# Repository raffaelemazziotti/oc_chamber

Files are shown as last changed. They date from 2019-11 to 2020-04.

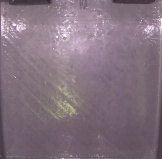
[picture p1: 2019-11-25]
LCD_oc_chamber/template.jpg

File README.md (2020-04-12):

# Operant Conditioning Chamber

Operant conditioning is a classical paradigm used in experimental psychology in which animals learn to perform an action in order to achieve a reward. By using this paradigm, it is possible to extract learning curves and measure accurately reaction times.
Here we describe a fully 3D printable device that is able to perform operant conditioning on  freely moving mice, while performing real-time tracking of the animal position.

## Assembling & Installation

You can find 3D printed models [here](https://github.com/raffaelemazziotti/oc_chamber/tree/master/3D_models) or [here](https://www.thingiverse.com/thing:3975752).  
In [figures/EXPLODED VIEW.jpg](https://github.com/raffaelemazziotti/oc_chamber/blob/master/figures/EXPLODED%20VIEW.jpg) there is an intuitive diagram of the assembling scheme.
We printed all the components using Cura 4.0 with a medium resolution (100 µm), a speed of 90 mm/s and an infill of 20%. The design of the OC chamber is quite simple so almost all the printers are sufficiently precise to successfully print the entire chamber.

A list of all the components can be found here: [Bill of materials](https://docs.google.com/spreadsheets/d/19AH2Pe1oMEcGUEE4mrs1yGA2-vNfwtRM7asQJUQdpgM/edit?usp=sharing)

### 3D printed parts

* **OC CHAMBER**
  * **arena:** main arena
  * **arena_holes:** main arena with holes on the floor
  * **barrier_posterior:** posterior barrier for jumpig mice
  * **frontal_wall_LED:** interface wall for LED matrix
  * **frontal_wall_LCD:** interface wall for LCD screen
  * **mask_dots:** mask for LED matrix
  * **touch_sensor:** button
* **CAMERA**
  * **cam_barrier:** camera holder with frontal barrrier for jumping mice
  * **cam_ladder:** 3d printed arm
  * **cam_holder:** camera holder
  
* **DELIVERY**
  * **delivery_base:** syringe and motor holders
  * **delivery_motor2thread:** thread to motor adapter
  * **delivery_piston:** syringe piston

In addition you need:

* a 1000 µF capacitor
* two 25 Mohm resistors for the touch buttons
* a 220 ohm resistor for the LED matrix
* a piece of M8 thread (~15 cm) for reward delivery

Connect all the components as described in [figures/diagram_scheme.png](https://github.com/raffapaz/oc_chamber/blob/master/figures/diagram_scheme.png)

To install the software in the Raspberry Pi(RPI) just download or copy the entire code in a folder of the Raspian OS.  

### Required libraries

Python

* [picamera](https://picamera.readthedocs.io/en/release-1.13/)
* [pySerial](https://pythonhosted.org/pyserial/)
* [openCV](https://pypi.org/project/opencv-python/)
* [Tkinter](https://tkdocs.com/tutorial/install.html)

Arduino

* [CapacitiveSensor](https://playground.arduino.cc/Main/CapacitiveSensor/)
* [Adafruit_NeoPixel](https://learn.adafruit.com/adafruit-neopixel-uberguide/arduino-library-use)
* [Stepper](https://www.arduino.cc/en/reference/stepper)

### Arduino Configuration

Compile and load on the [Arduino UNO](https://store.arduino.cc/arduino-uno-rev3) the sketch called [skinner.ino](https://github.com/raffaelemazziotti/oc_chamber/tree/master/arduino_files/skinner)

### Capacitive Sensors calibration

To calibrate [capacitive sensors](https://en.wikipedia.org/wiki/Capacitive_sensing) thresholds load the Arduino sketch called [skinnerCapacitiveTest](https://github.com/raffaelemazziotti/oc_chamber/tree/master/arduino_files/skinnerCapacitiveTest). This function just prints on the serial port capacitive sensor values. It is helpful to set the proper threshold value to detect mouse touches.

### Running Python code

To run the code type in terminal:

```bash
cd \home\pi\oc_chamber\         \\ or replace with the folder path containing the scpript
python3 cvConditioningTracking.py
```

Alternatively open cvConditioningTracking in [IDLE](https://en.wikipedia.org/wiki/IDLE) IDE and push F5.

The user can customize some of the low-level parameters of the experiments by editing the value of the variables in the first 25 lines of the file [cvConditioningTracking](https://github.com/raffaelemazziotti/oc_chamber/blob/master/cvConditioningTracking.py).py. A more detailed explanation of those parameters is given in the file itself.

The chamber can run experiments in 2 modes: **Training** mode and **Permutation** mode. The user can select one of the two modes by editing the parameter **task** in the cvConditioningTracking file. The details and differences of the 2 modes can be found in the [paper](#references).

### Experiment info GUI

At the start of the experiments, the user is prompted with a GUI that collects some basic informations about the experiments that is about to run.

Screenshot of the GUI for selecting some basic experiment informations.

* **Subject:** A string containing an identifier for the current mouse. If left empty no file is saved.
* **File Path:** Location to save experiment file. The output consists of two .txt files containing the dataset of the experiment as described in the [dataset](#dataset) section,stored inside DATA and DATAtracker folder. The user can browser for a location on the PC, if the field is left empty the default is the current working directory.
* **REC file name:** A string containing the name to use for saving the video recording. If left empty no file is saved.
* **REC file path:** Location to save the video recording with an overlay containing the mouse position and the active area. The user can browser for a location on the PC, if the field is left empty the default is the current working directory.
* **Conditions:** Experimental conditions. The list of stimuli that will be presented in the experiment. One or more conditions, divided by a comma, can be specified:

  * right: right dot
  * left: left dot
  * both: dots on the right and left simultaneously

  All the conditions specified here will be presented in a random order.

* **Criterion:** Number of frames necessary for the mouse to stay in the active area to activate a trial. 20 frames = 1 sec
* **Level:** Select the vertical position of the line segregating the active area of the chamber from the inactive one. The value is normalized to the chamber height. 0 = bottom of the chamber, 1 = top of the chamber, 0.5(default) = middle of the chamber
* **Calibration:** Number of frames to be used at the beginning of the experiment for camera calibration. Calibrating the camera at the beginning of the experiment is important to better track the mouse over the background.

### Other Settings

Other customization options are available by editing the first lines of the following files:

* **cvConditioningTracking** (to change computer vision parameters and type of procedure between TRAINING or PERMUTATION )
* **skinner** (stimulus permanence, button threshold)
* **skinnerCapacitiveSensor** (change the button to check and the threshold)

## LCD_oc_chamber

To allow the use of more complex visual stimuli you can find a backbone version of the code that works with an [LCD display](http://kookye.com/2016/08/01/kookye-3-5-touch-screen-for-raspberry-pi-display-monitor-480x320-lcd-touchscreen-kit-3-5lcd-pi-2-board-case/). To run the code [Psychopy2](https://www.psychopy.org/) is required. To install Psychopy on RPI follow [these](https://www.psychopy.org/download.html) instructions. Once Psychopy is installed open cvConditioningTracking.py in the Psychopy IDE and run the code. This code contains a module called LCD.py that can be used to show selected images. For now, the code is a stub, an untested version and runs for demonstrative purposes.

## Keyboard Shortcuts

* **p**: exit from program (p keypress skips camera calibration when in the "camera calibration" phase, otherwise it closes the program)
* **s**: stop a trial

## Dataset

[Dataset](https://github.com/raffaelemazziotti/oc_chamber/tree/master/dataset) folder contains our raw data, described in this [paper](#references), with 6 subjects. Each subject is contained in its own folder and coded using the scheme: CAGE-LABEL-GENO. Furthermore, there are two Jupyter Notebooks with an example on how you can read txt output files in Python as [pandas](https://pandas.pydata.org/) dataframes.

* **data:** contains folders representing subjects. In the folder there are .txt files with fields
  * Event - the type of event (both,single)
  * Answer - the answer provided by the subject (both_sx,both_dx,yes,no)
  * RT - Reaction time
  * Time - Timestamp
* **data_track:** contains the real time tracking of the animal position. The first row represents the borders of the arena (rect x, y, x+width, y+height).
The rest of the lines contain
  * timestamp - timmestamp
  * x - x coordinate
  * y - y coordinate
  * event - type of event (both,left,right)

## Authors

* [**Raffaele Mazziotti**](https://github.com/raffaelemazziotti)
* **Giulia Sagona**  
* [**Leonardo Lupori**](https://github.com/leonardolupori)
* **Virginia Martini**
* [**Tommaso Pizzorusso**](https://www.researchgate.net/profile/Tommaso_Pizzorusso)

## References

Detailed description of the apparatus can be found here:
[3D printable device for automated operant conditioning in the mouse](https://www.eneuro.org/content/early/2020/04/06/ENEURO.0502-19.2020)

## Contacts

For any info and troubleshooting don't hesitate to contact us at

* raffaele.mazziotti@in.cnr.it
* leonardo.lupori@sns.it
* giulia.sagona@in.cnr.it

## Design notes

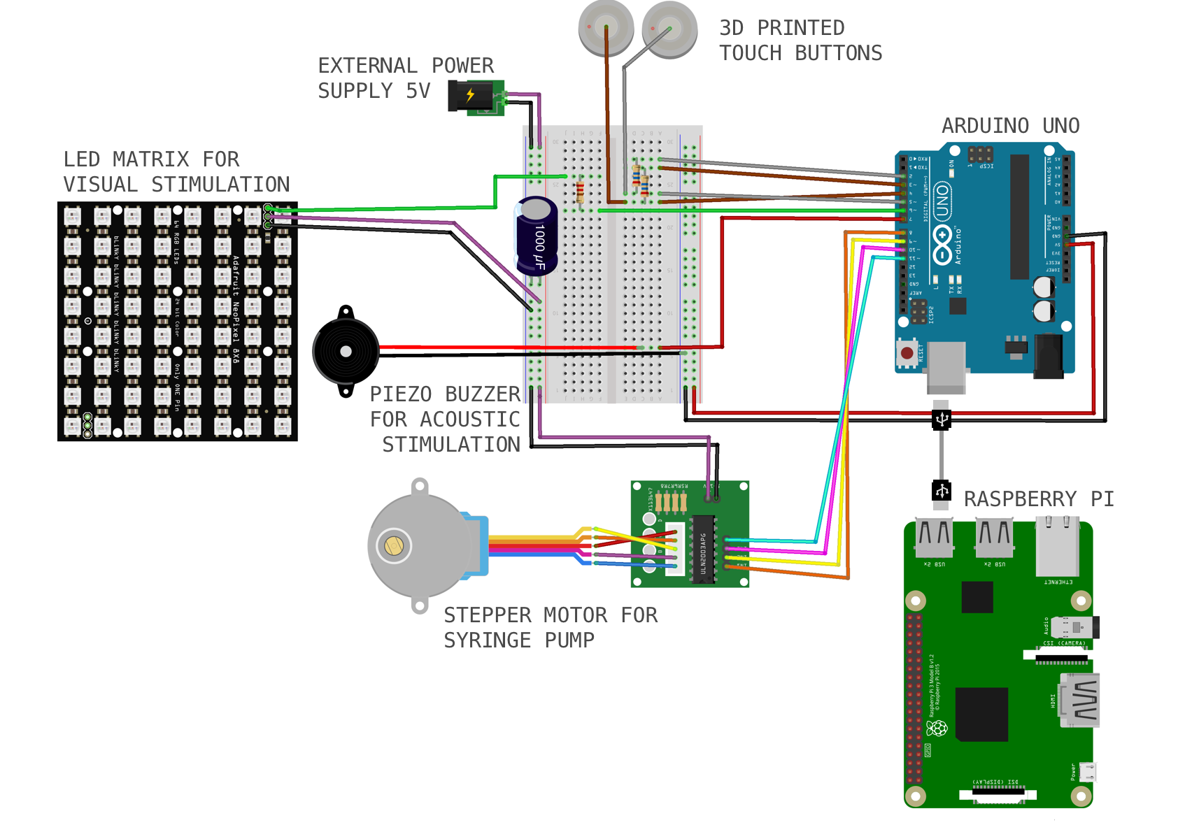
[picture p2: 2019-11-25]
figures/diagram_scheme.png

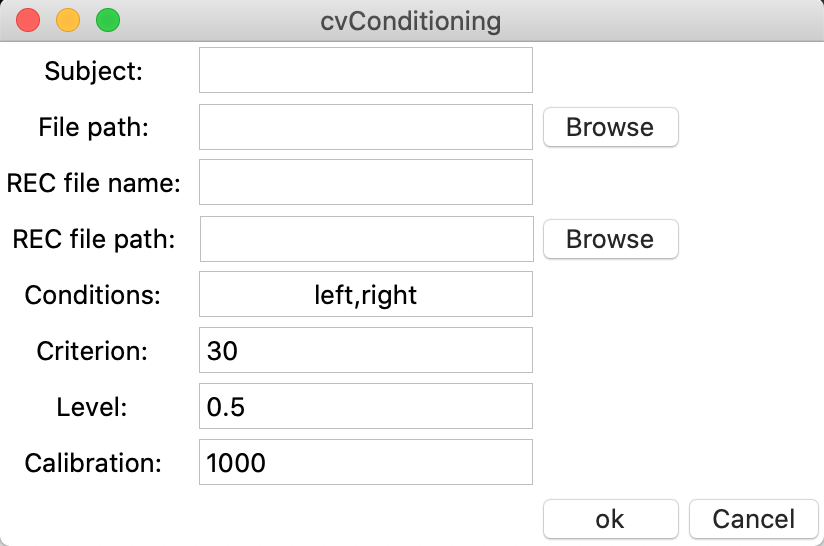
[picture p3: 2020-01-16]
gui_example.png

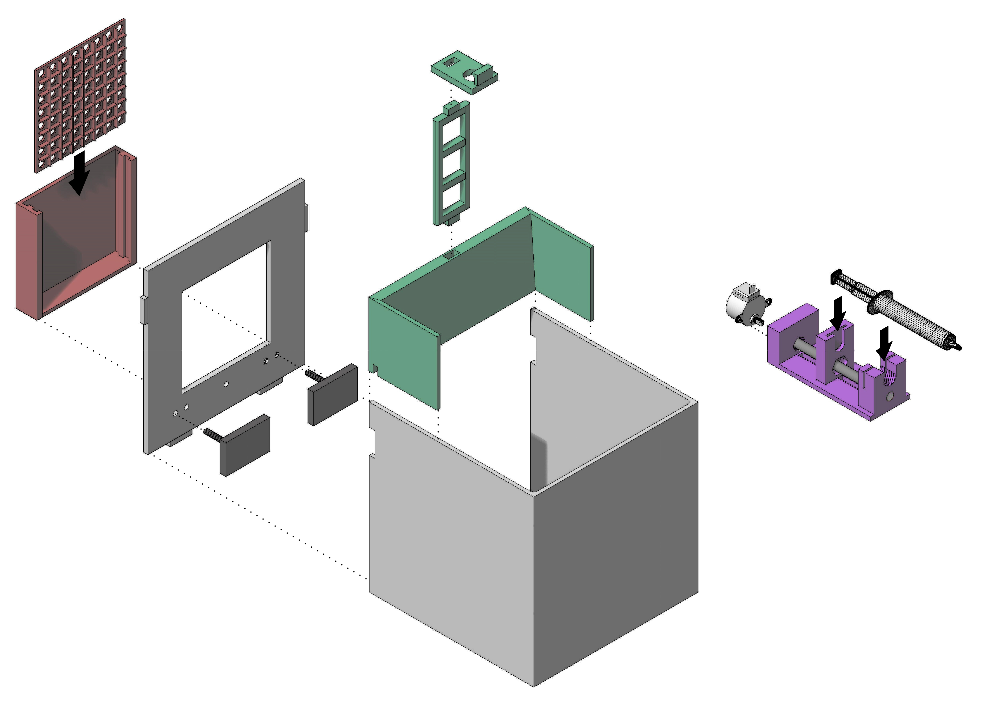
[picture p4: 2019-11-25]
figures/EXPLODED VIEW.jpg

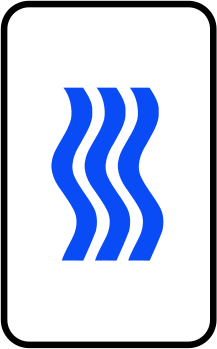
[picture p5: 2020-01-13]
LCD_oc_chamber/zener/waves.png

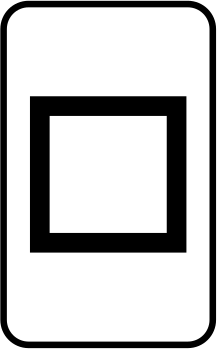
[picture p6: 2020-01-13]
LCD_oc_chamber/zener/square.png

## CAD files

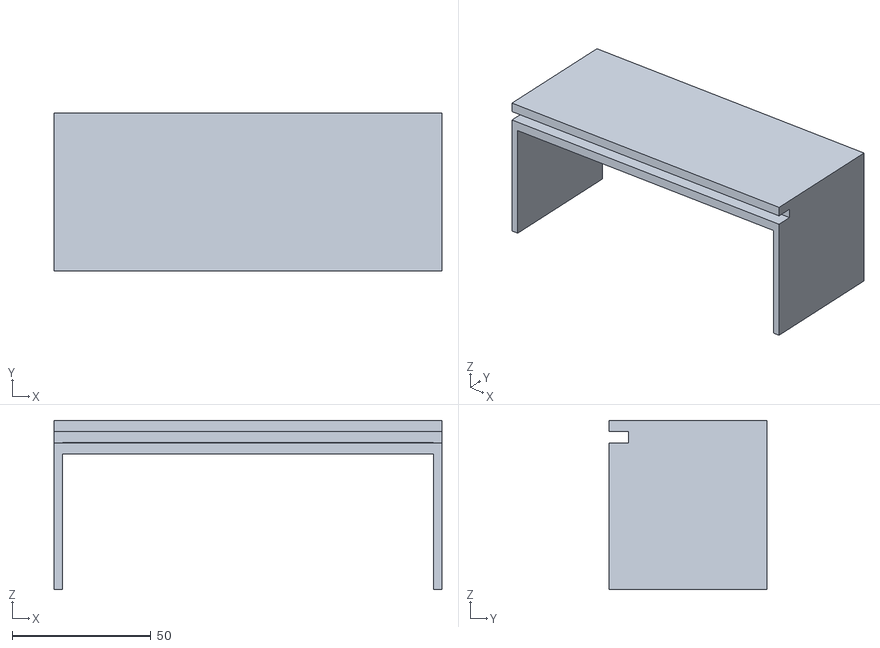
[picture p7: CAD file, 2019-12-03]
3D_models/camera/cam_barrier.stl
140.0 x 57.0 x 61.0

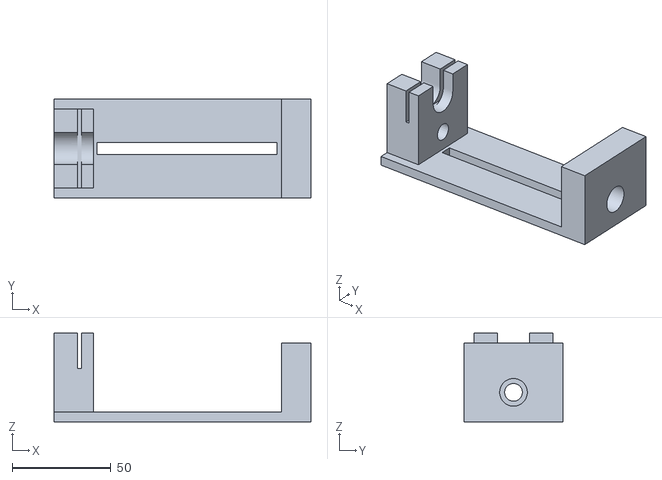
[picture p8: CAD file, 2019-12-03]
3D_models/delivery/delivery_base.stl
130.0 x 50.0 x 45.0

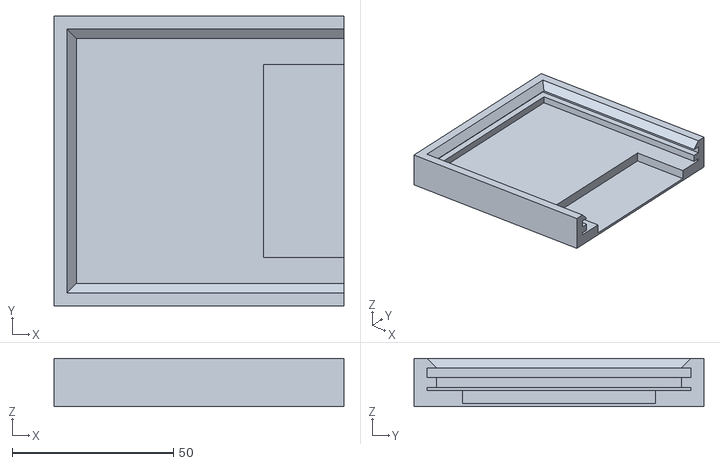
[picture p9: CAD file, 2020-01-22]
3D_models/OC_chamber/LED_holder.stl
90.0 x 90.0 x 15.0

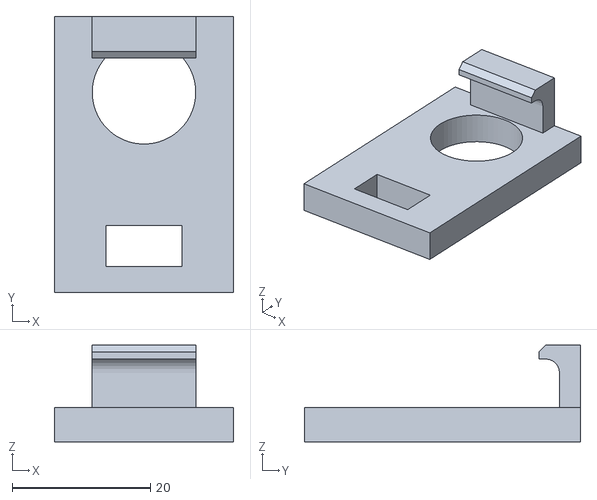
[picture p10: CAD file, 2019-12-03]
3D_models/camera/cam_holder.stl
26.0 x 40.0 x 14.0

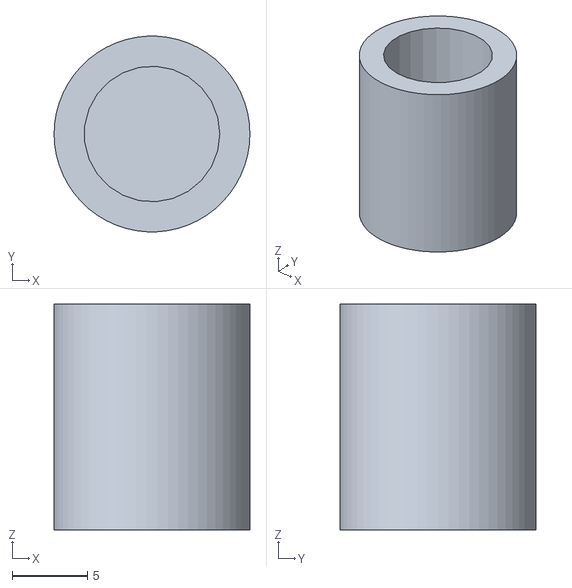
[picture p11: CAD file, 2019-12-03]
3D_models/delivery/delivery_motor2thread.stl
13.0 x 13.0 x 15.0

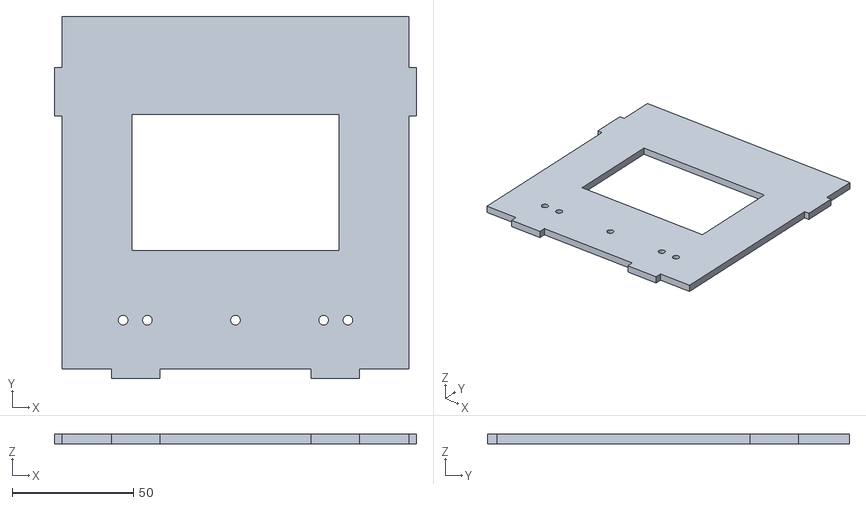
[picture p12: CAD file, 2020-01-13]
3D_models/OC_chamber/frontal_wall_LCD.stl
149.0 x 149.0 x 4.00

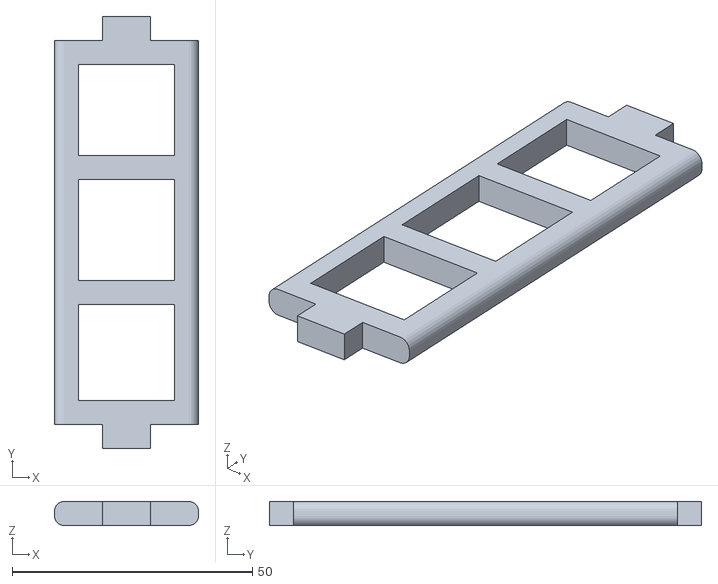
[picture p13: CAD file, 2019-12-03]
3D_models/camera/cam_ladder.stl
30.0 x 90.0 x 5.00

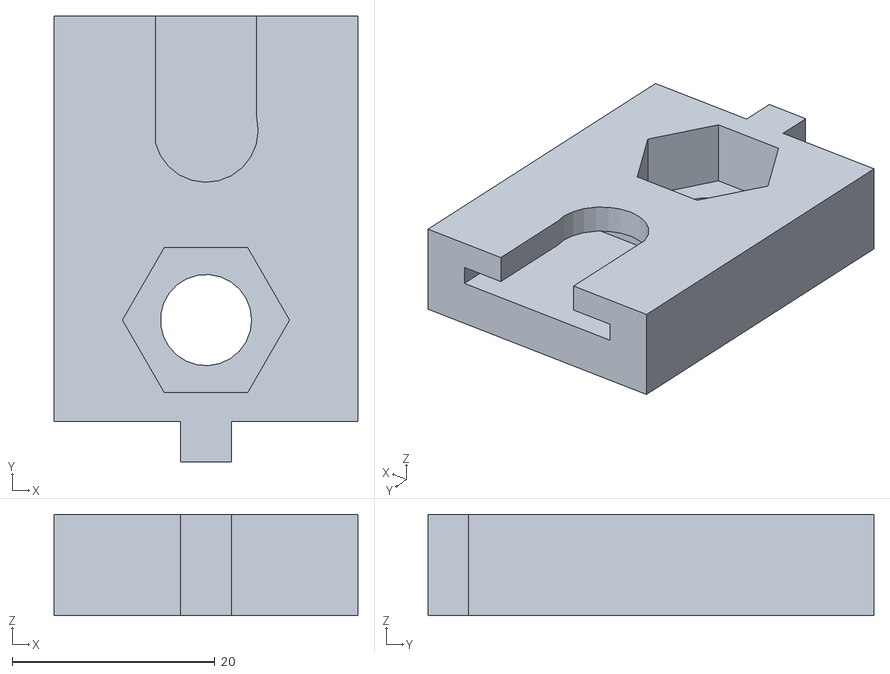
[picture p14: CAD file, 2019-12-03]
3D_models/delivery/delivery_piston.stl
30.0 x 44.0 x 10.0

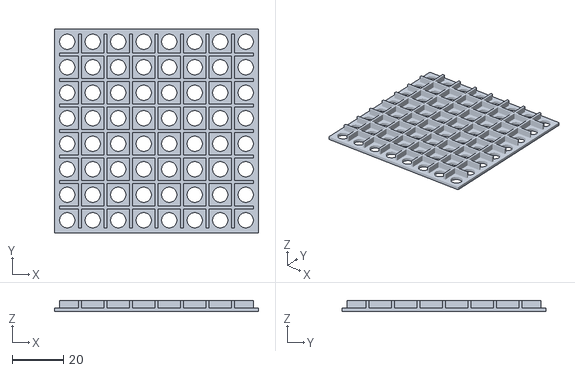
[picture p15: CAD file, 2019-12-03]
3D_models/OC_chamber/mask_dots.stl
80.0 x 80.0 x 4.50

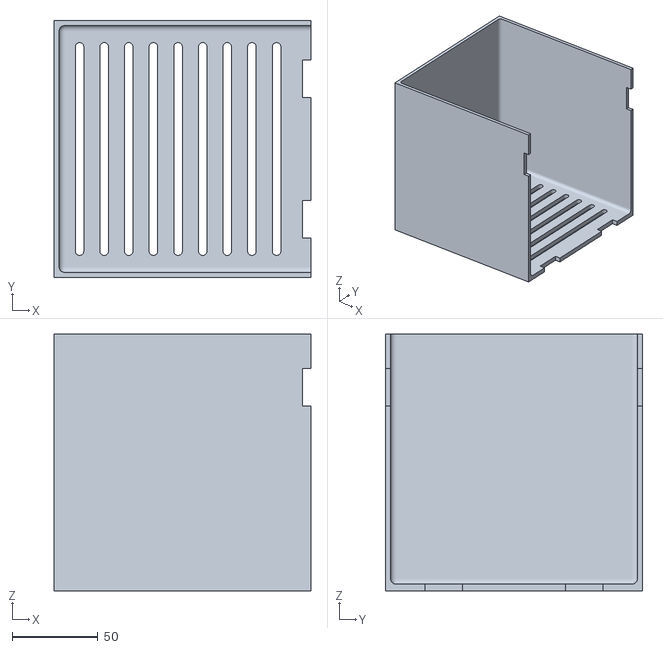
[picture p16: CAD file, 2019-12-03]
3D_models/OC_chamber/arena_holes.stl
150.0 x 150.0 x 150.0

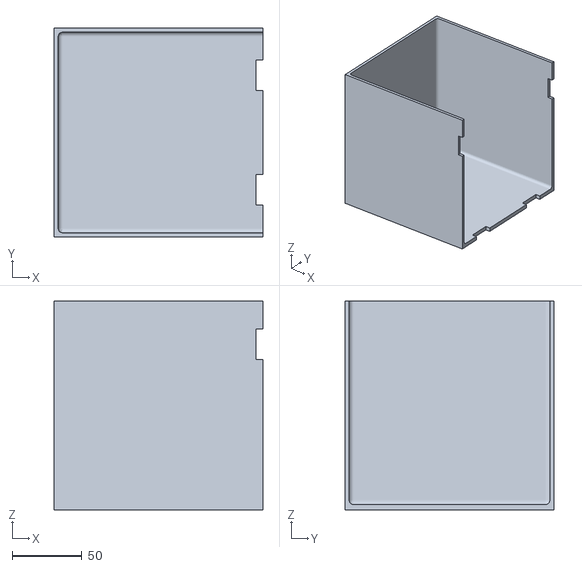
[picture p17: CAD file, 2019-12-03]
3D_models/OC_chamber/arena.stl
150.0 x 150.0 x 150.0

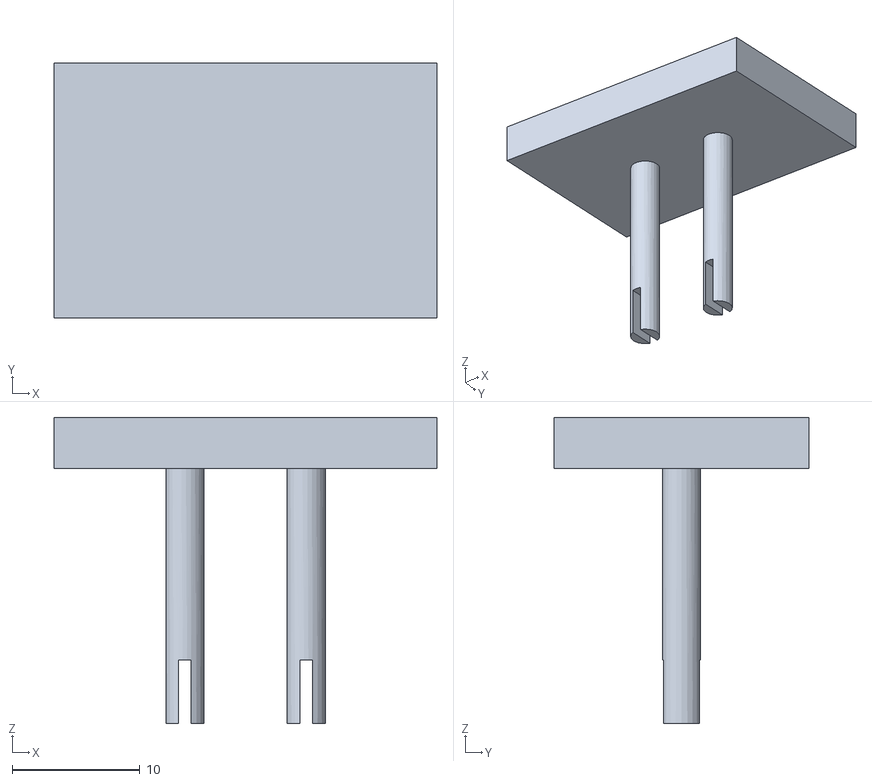
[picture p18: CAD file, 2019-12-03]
3D_models/OC_chamber/touch_sensor.stl
30.0 x 20.0 x 24.0

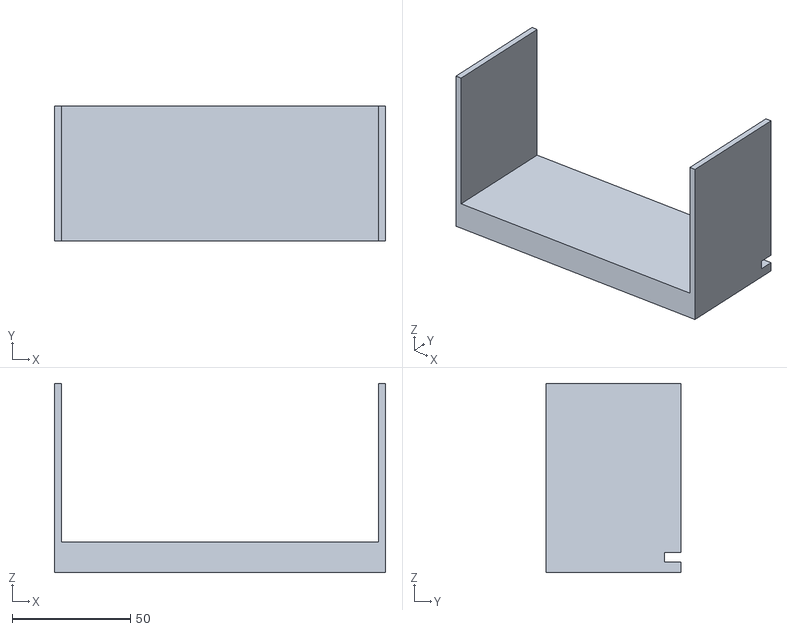
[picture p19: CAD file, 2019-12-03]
3D_models/OC_chamber/barrier_posterior.stl
140.0 x 57.0 x 80.0

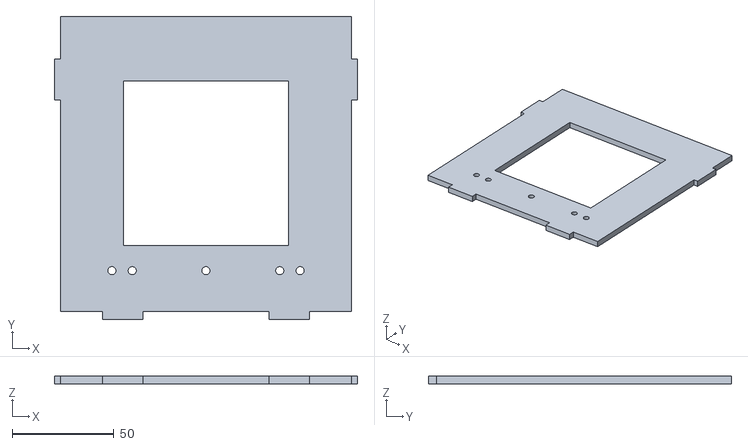
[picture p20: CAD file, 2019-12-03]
3D_models/OC_chamber/interface_wall_LED.stl
149.0 x 149.0 x 4.00

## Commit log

2019-12-03 code clean
    [arena.stl, arena_holes.stl, barrier_posterior.stl, cam_barrier.stl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]
2020-01-10 arduino lcd
2020-01-13 LCD and readme
    lcd frontal wall
    [frontal_wall_LCD.stl, interface_wall_LED.stl]
2020-01-15 readme changed
    [arena.stl, arena_holes.stl, barrier_posterior.stl, frontal_wall_LCD.stl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]
